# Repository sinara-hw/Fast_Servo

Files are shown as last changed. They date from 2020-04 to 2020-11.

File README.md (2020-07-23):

# Fast_Servo

High speed low latency servo (Stabilizer-compatible) module

## Design Files

Design files (schematics, PCB layouts, BOMs) can be found at [Fast_Servo/Releases](https://github.com/sinara-hw/Fast_Servo/releases).

## Wiki

More information can be found on the [wiki](https://github.com/sinara-hw/Fast_Servo/wiki).

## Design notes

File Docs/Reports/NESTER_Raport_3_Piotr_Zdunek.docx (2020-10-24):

Projekt „Niskolatencyjny, synchroniczny i skalowalny system SDR” (NESTER)

Piotr Zdunek

Raport z pracy o dzieło z prawami autorskimi pt.:
„ Opracowanie firmware FPGA dla modułu EEM z układem FPGA”
zrealizowanej w okresie od 04.05.2020 r. do 26.05.2020 r.
Pracę wykonał Piotr Zdunek

Celem pracy było opracowanie schematów i PCB modułu EEM z układem FPGA oraz symulacje systemu cyfrowego.

Trzeci etap prac zawierał następujące zadania:

- realizację schematów elektrycznych
- symulacje front-endu analogowego do przetwornika DAC
- projekt PCB

Wynikiem pracy są:

- Schematy elektryczne – ukończone w 100% - wymagają recenzji
  - https://github.com/sinara-hw/Fast_Servo/tree/master/PCB
- Projekt PCB – wstępne prace, ułożenie podstawowych komponentów, ustalenie ilości warstw
- Oprogramowanie testowe będzie przygotowane przy dalszym rozwinięciu projektu PCB
  - https://github.com/sinara-hw/Fast_Servo/tree/master/Sim/fast_servo
- Raport z symulacji front-endu przetwornika DAC (po angielsku)
  - https://docs.google.com/document/d/1JZjIepW1oN7cgWxagVTp9rN9icUm_Yqzp_lJ3G2Z5V4/edit?usp=sharing

1. Schematic:

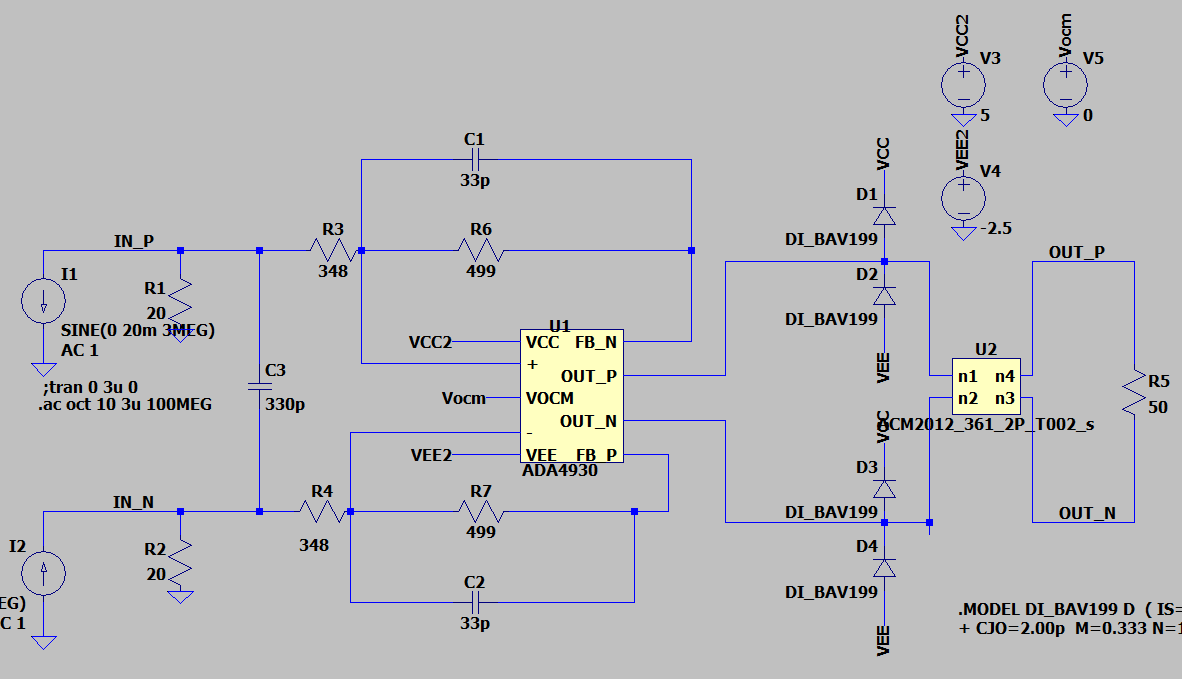
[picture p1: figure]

  1. Sim file for transient (with Monte Carlo simulation):

https://www.dropbox.com/s/zismo5z99h6hax0/ada4930_afe_tran_mc.asc?dl=0

  b. Sim file for AC(with Monte Carlo simulation):

https://www.dropbox.com/s/ytwsxa8ljqnvvi3/ada4930_afe_ac_mc.asc?dl=0

  c. Sim file for step (with Monte Carlo simulation) https://www.dropbox.com/s/y0xfj7qcieoy4dm/ada4930_afe_step_mc.asc?dl=0
2. Transient simulation:
    1. Common parameters: input signal is sinus for current sources
    2. Plot for 3 MHz 20 mA input signal

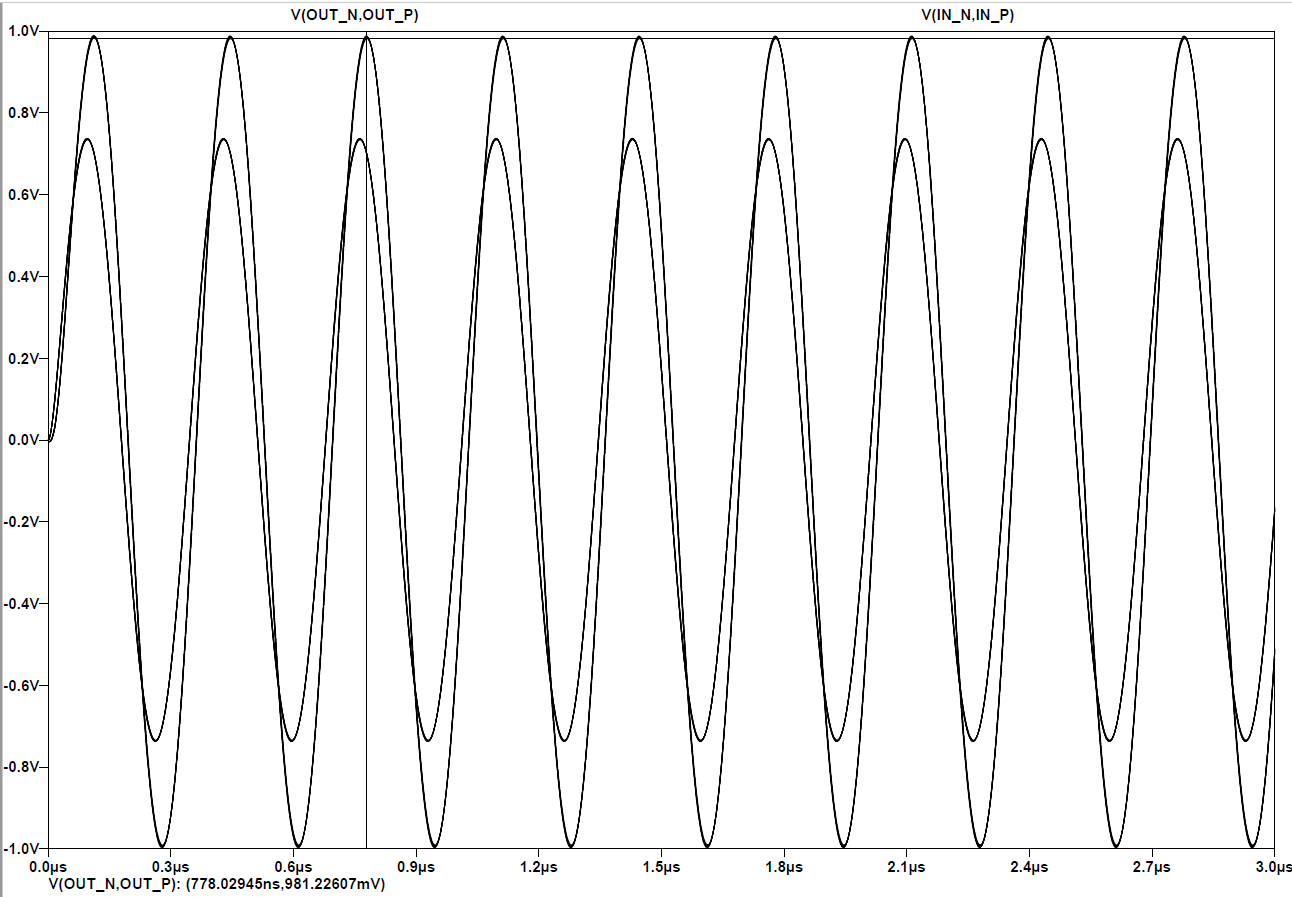
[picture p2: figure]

Simulation results:

Input signal | | Output signal
Freq [MHz] | Amplitude [mA] | Output amplitude [mV]
3 | 20 | 981
1 | 20 | 1059

3. AC simulation:

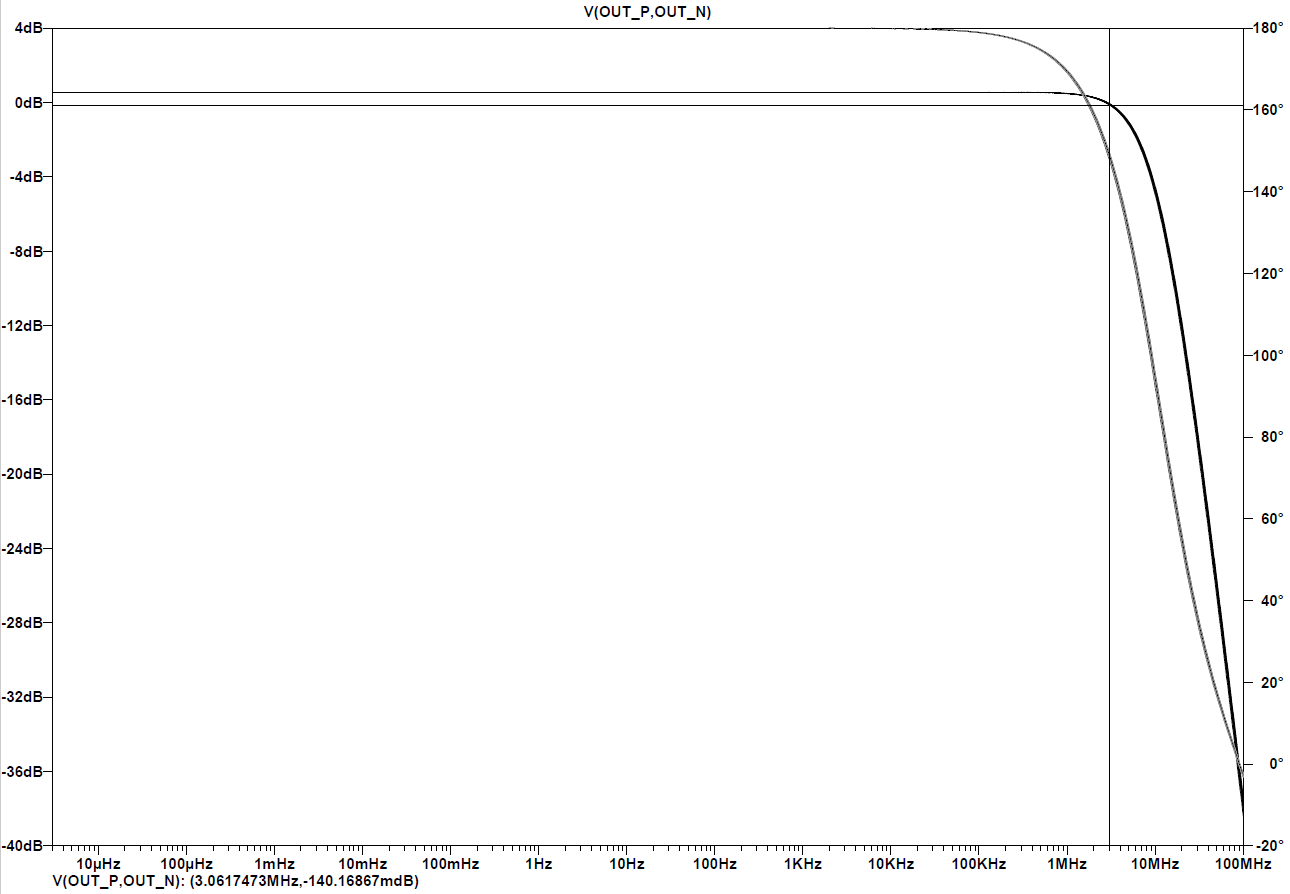
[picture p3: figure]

Simulation results:

Input signal amplitude [mA] | Attenuation at 1 MHz [dB] | Attenuation at 3 MHz [dB]
20 | 0.486 | -0.140

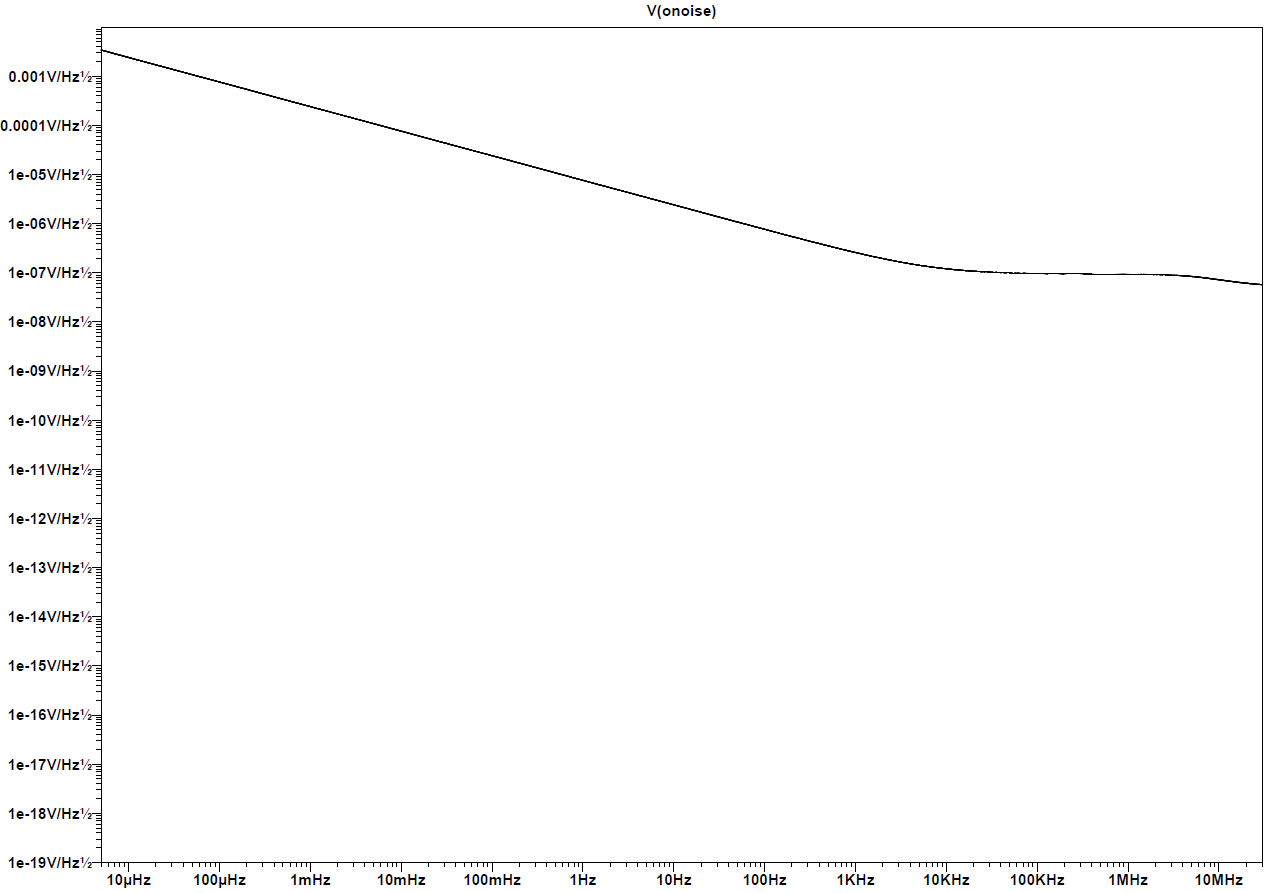
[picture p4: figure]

Plot for 1V input signal, Monte Carlo part value variance, 10 runs

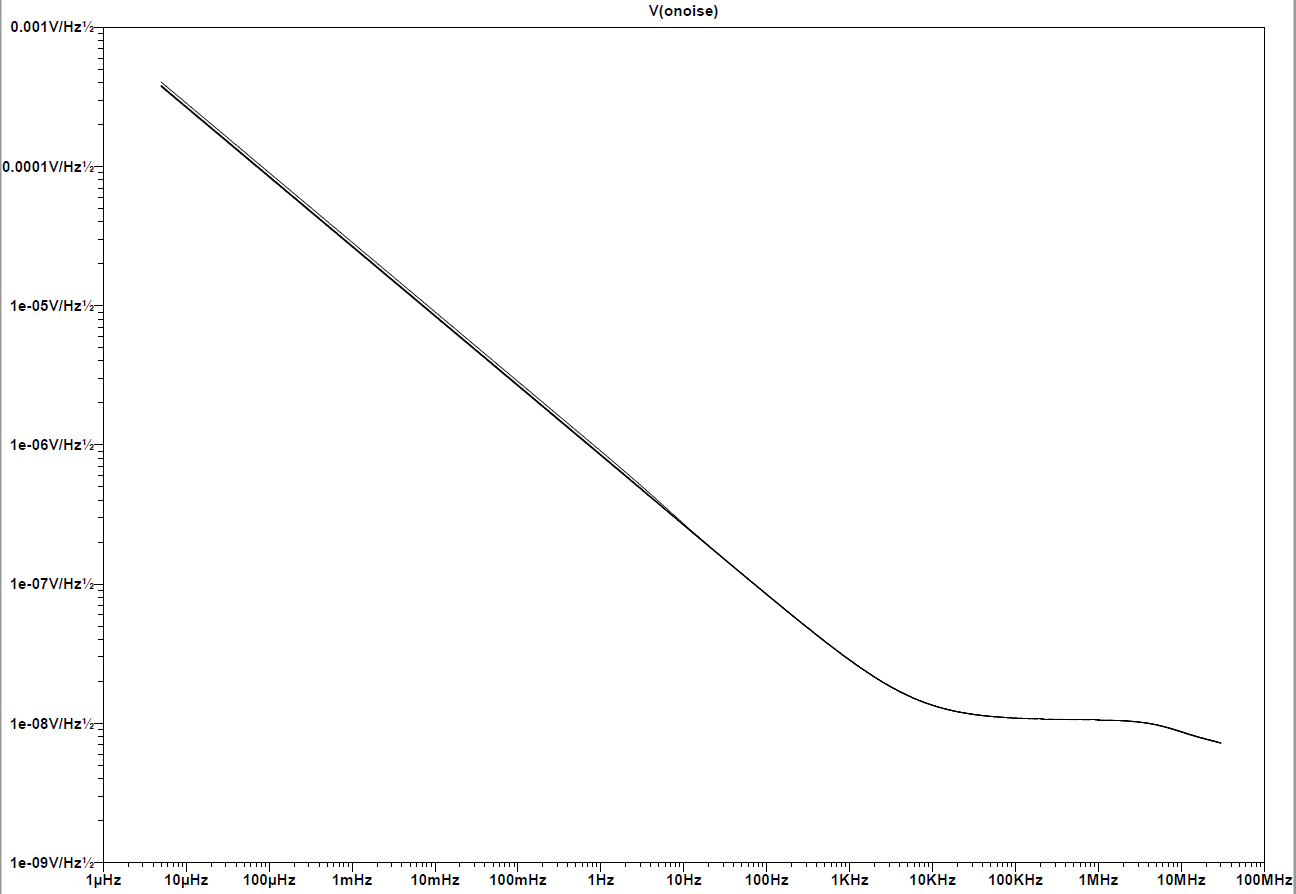
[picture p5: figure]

- Schemat elektryczny urządzenia zawierający dobrane komponenty:
  - Top schematic

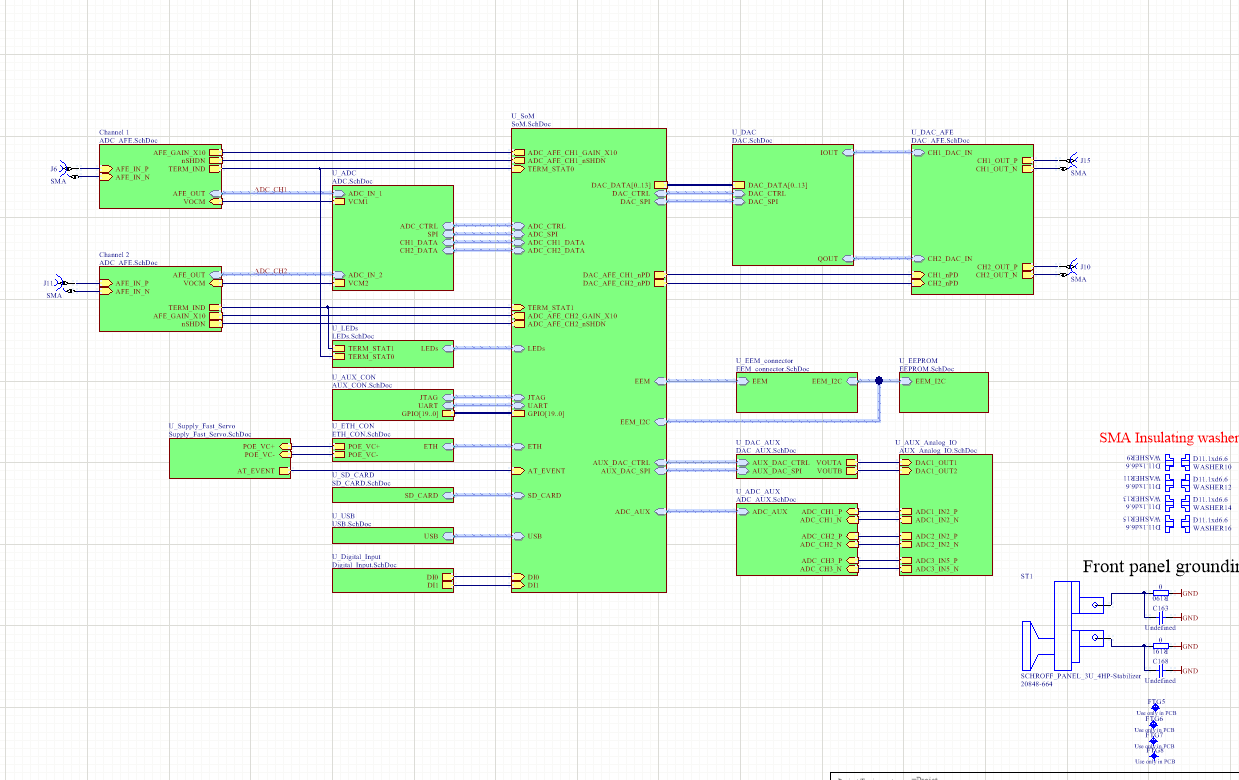
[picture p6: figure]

- ADC AFE

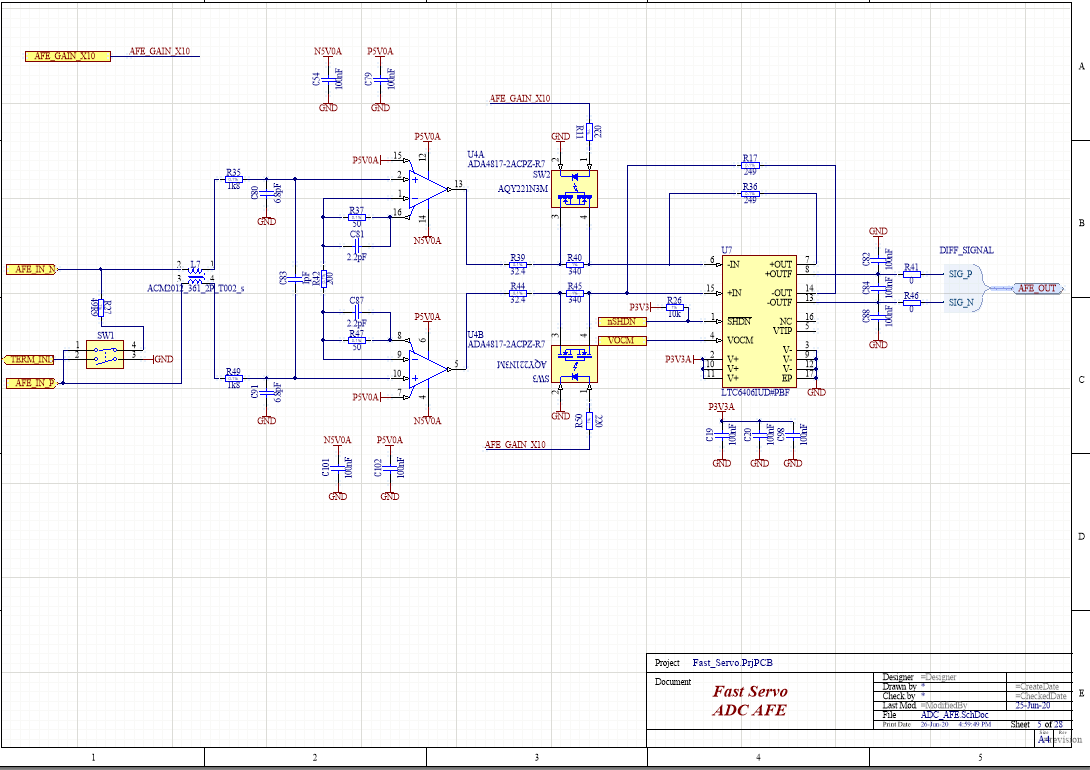
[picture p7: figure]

- DAC AFE

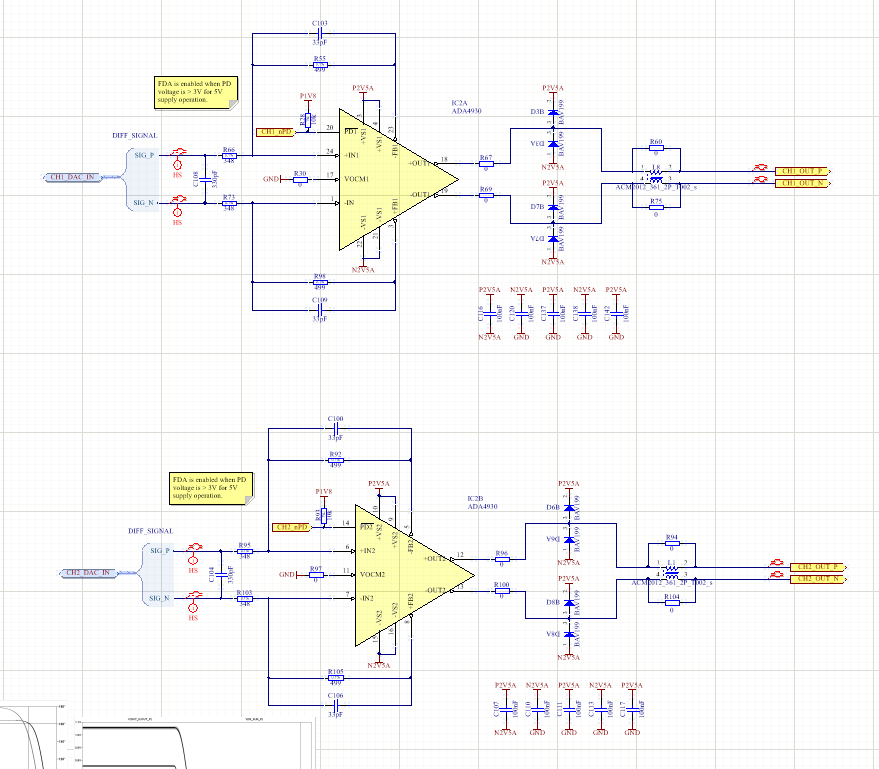
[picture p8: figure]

- PCB

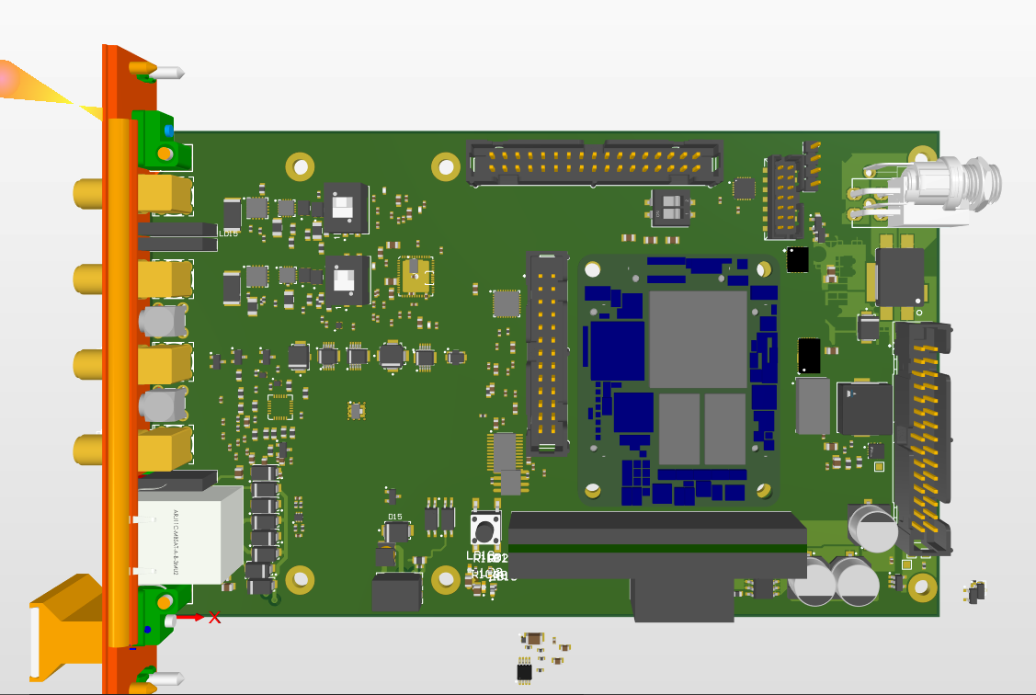
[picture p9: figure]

Spis treści

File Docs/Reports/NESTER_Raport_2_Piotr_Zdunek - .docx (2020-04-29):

Projekt „Niskolatencyjny, synchroniczny i skalowalny system SDR” (NESTER)

Piotr Zdunek

Raport z pracy o dzieło z prawami autorskimi pt.:
„ Opracowanie wzoru obwodu PCB oraz weryfikacja połączeń HDL modułu
EEM z układem FPGA”
zrealizowanej w okresie od 02.03.2020 r. do 28.04.2020 r.
Pracę wykonał Piotr Zdunek

Celem pracy było opracowanie schematów i PCB modułu EEM z układem FPGA oraz symulacje systemu cyfrowego.

Drugi etap prac zawierał następujące zadania:

- realizację schematów elektrycznych
- symulacje front-endu analogowego do przetwornika ADC
- symulacja systemu cyfrowego
- analiza opóźnienia odbioru danych

Wynikiem pracy są:

- Schematy elektryczne – ukończone w 70%
  - https://github.com/sinara-hw/Fast_Servo/tree/master/PCB
- Wstępny system cyfrowy do odbioru danych z LTC2195 oparty o design z projektu NIST Servo, ale z wykorzystaniem wrappera na VHDL
  - https://github.com/sinara-hw/Fast_Servo/tree/master/Sim/fast_servo

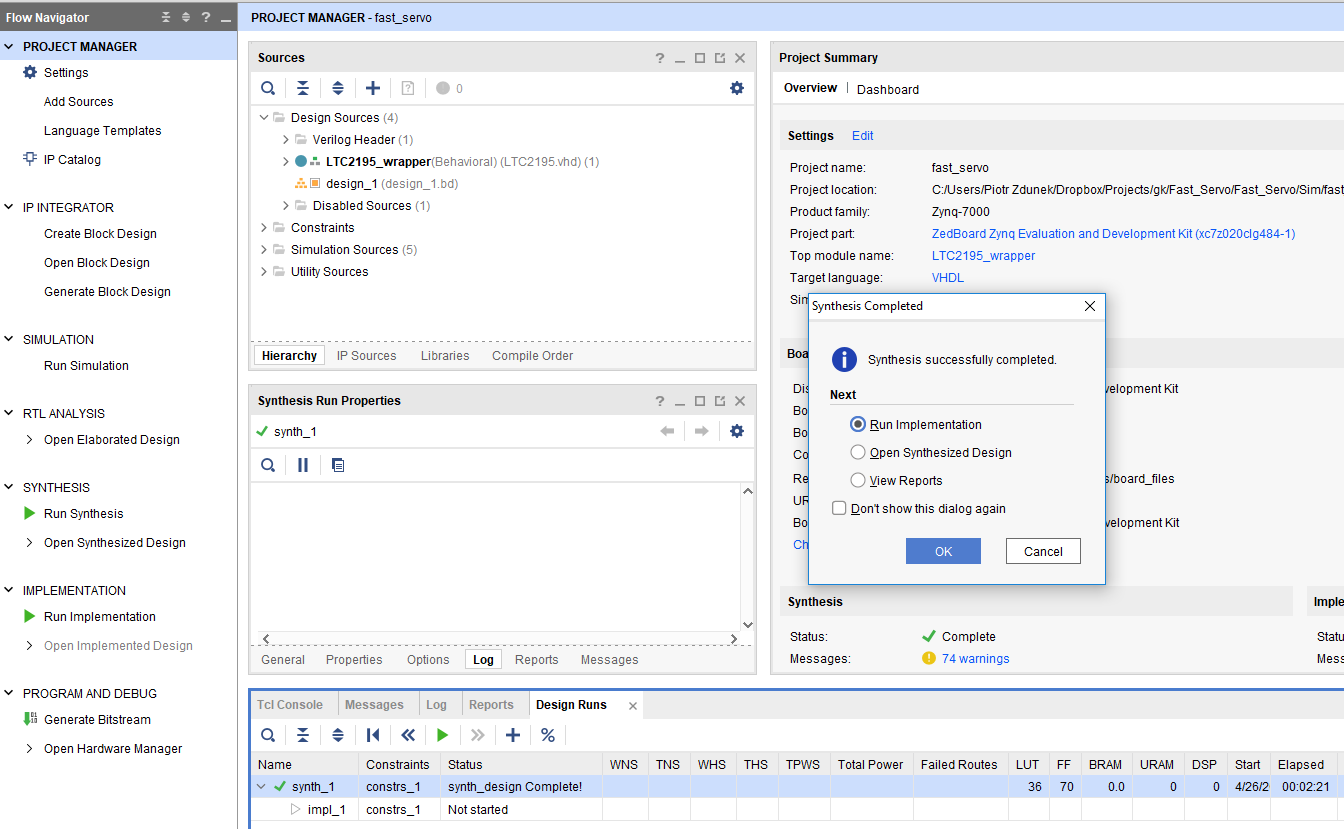
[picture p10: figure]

- Raport z symulacji front-endu przetwornika ADC (po angielsku)
  - https://docs.google.com/document/d/1smgiGiFC6XPziigHHxrSAG0CFXy-PrKfYR3dXpd6QYk/edit?usp=sharing

1. Variant 2 - RFI filter with common mode choke and differential low pass filter
  1. Schematic:

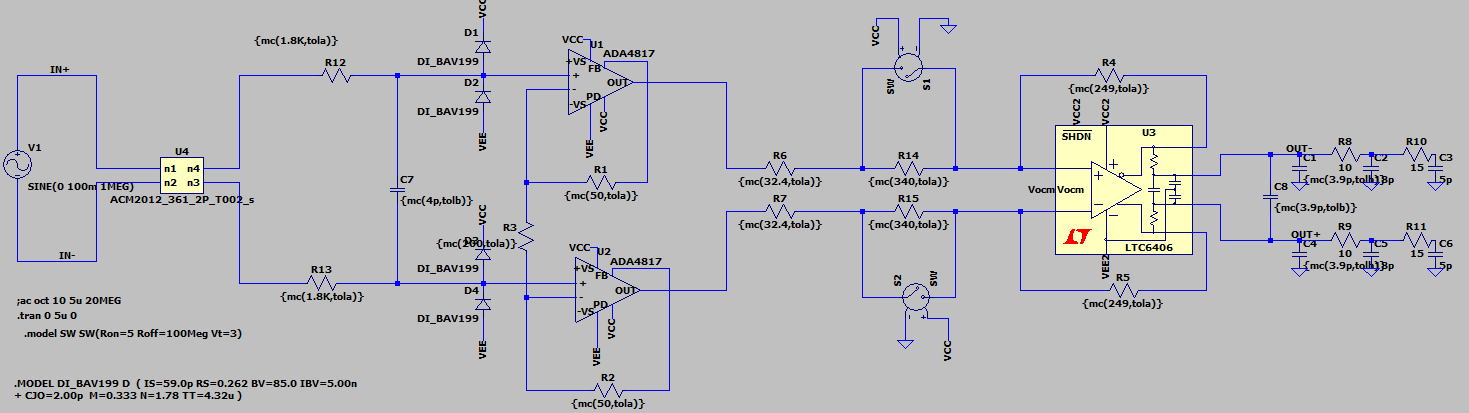
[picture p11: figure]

  b. Sim file for transient:

https://www.dropbox.com/s/ghg6t9eu0ng3u3w/fast_servo_tran_mc_v3.asc?dl=0

  c. Sim file for AC

https://www.dropbox.com/s/qx53d03kradoqxc/fast_servo_ac_v3.asc?dl=0

  d. Sim file for CMRR

https://www.dropbox.com/s/pwxwzrt2xnfyjam/fast_servo_cmrr_mc_v10.asc?dl=0

  e. Sim file for noise

https://www.dropbox.com/s/fyhz8l2sw5p7yvu/fast_servo_noise_mc_v3.asc?dl=0

Transient simulation:

Common parameters: input signal is sinus

Plot for 1 MHz 1 V input signal

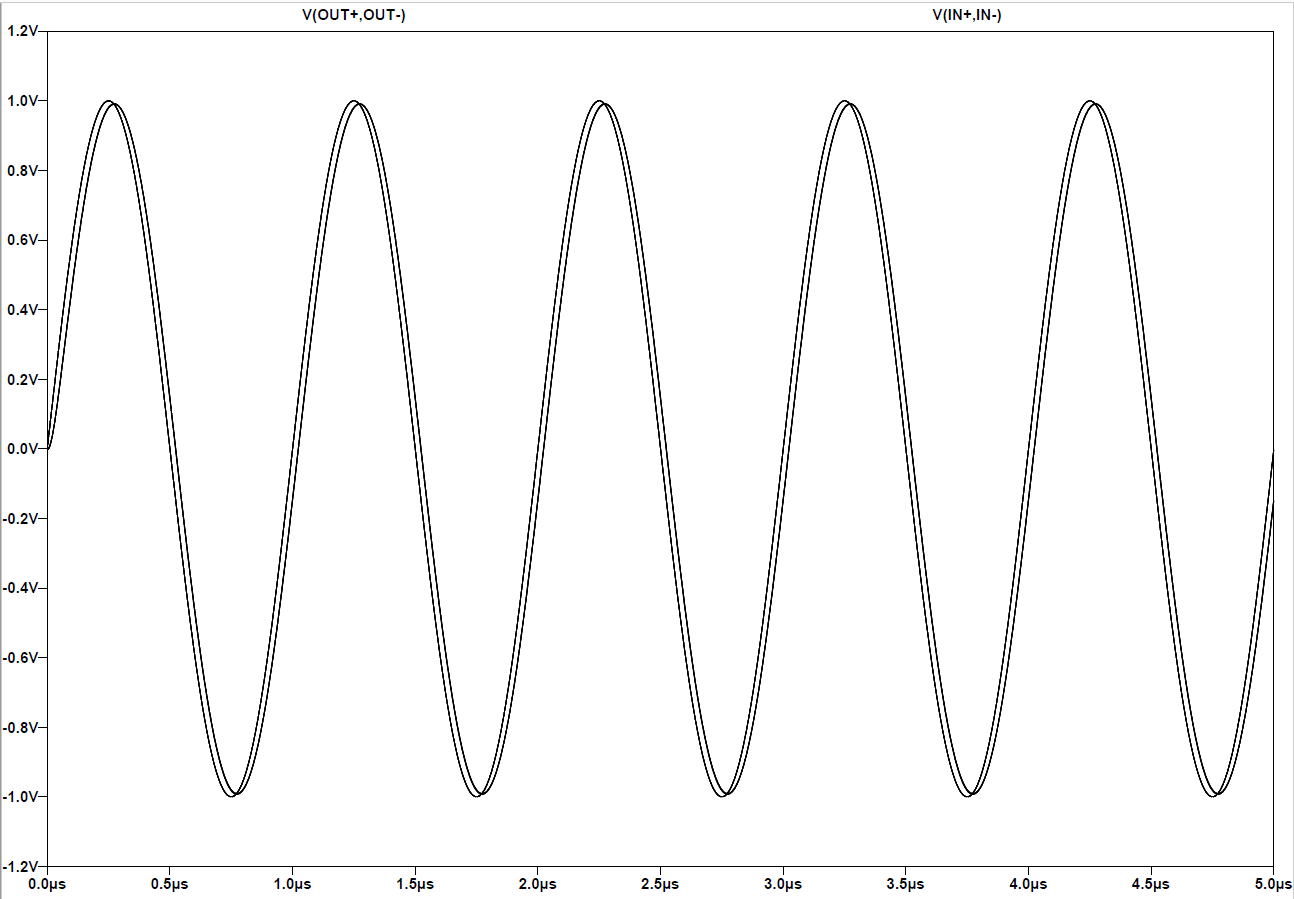
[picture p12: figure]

Simulation results:

Input signal | | AFE | Output signal
Freq [MHz] | Amplitude [mV] | Gain | Output amplitude [mV]
3 | 100 | x10 | 918
1 | 100 | x10 | 983
3 | 1000 | x1 | 925
1 | 1000 | x1 | 991

AC simulation:

Plot for 1V input signal, x1 gain

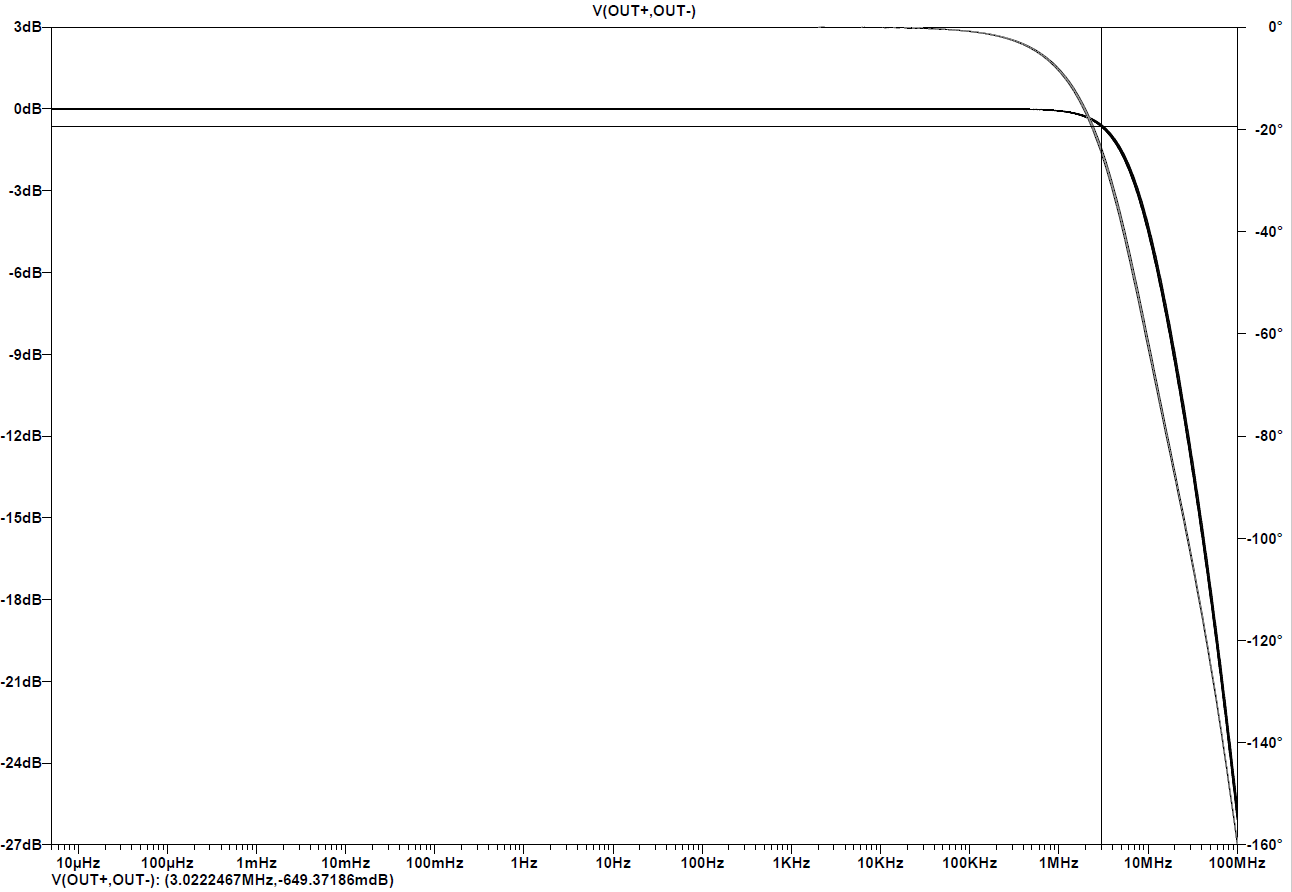
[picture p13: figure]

Simulation results:

Input signal amplitude [V] | AFE Gain | Attenuation at 1 MHz [dB] | Attenuation at 3 MHz [dB]
1 | x1 | -0.072 | -0.6
0.1 | x10 | -0.144 | -0.719

CMRR measurement:

Plot for 1 V input signal.

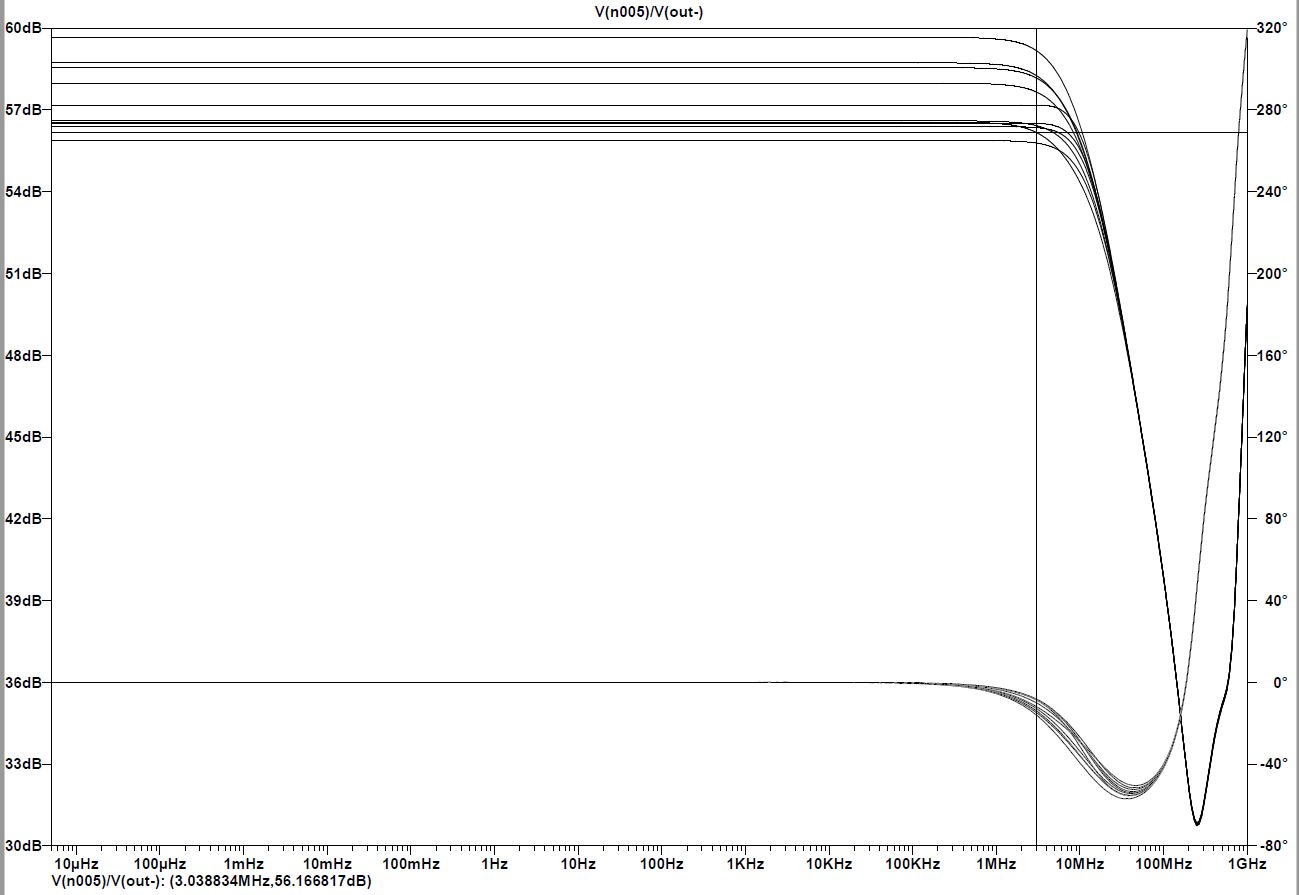
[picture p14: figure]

Simulation results:

Input signal amplitude [V] | AFE Gain | CMRR (0-3 MHz)
1 | x1 | 56 dB
0.1 | x10 | 49 dB

Noise

Plot for 100 mV input signal, Monte Carlo part value variance, 10 runs.


Plot for 1V input signal, Monte Carlo part value variance, 10 runs


- Analiza opóźnienia toru danych ADC-FPGA-DAC:

https://docs.google.com/document/d/1A6bej79ME2-iZyJ6t_FZ-XkVyk64ExRZh2uJX7Lg3b4/edit?usp=sharing

- Schemat elektryczny urządzenia zawierający dobrane komponenty:
  - Top schematic

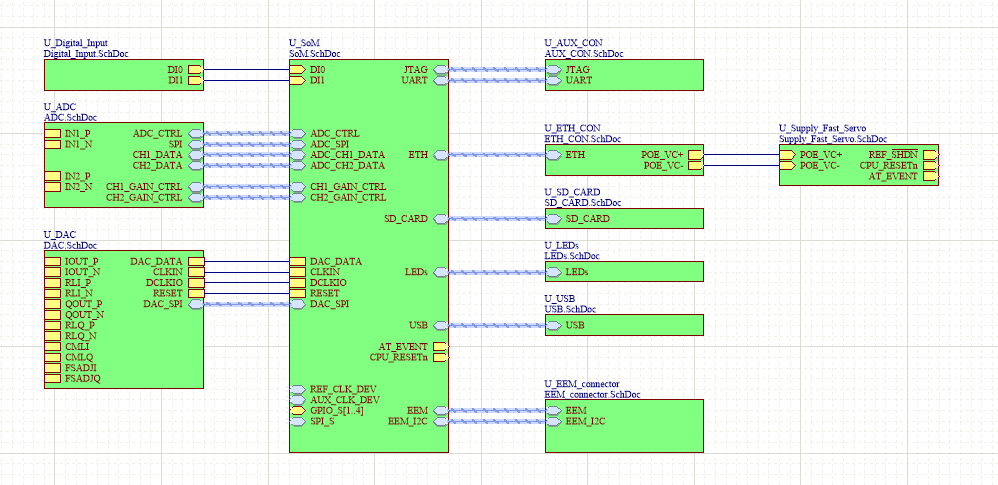
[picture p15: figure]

- Złącze Ethernet – 100 Mbps

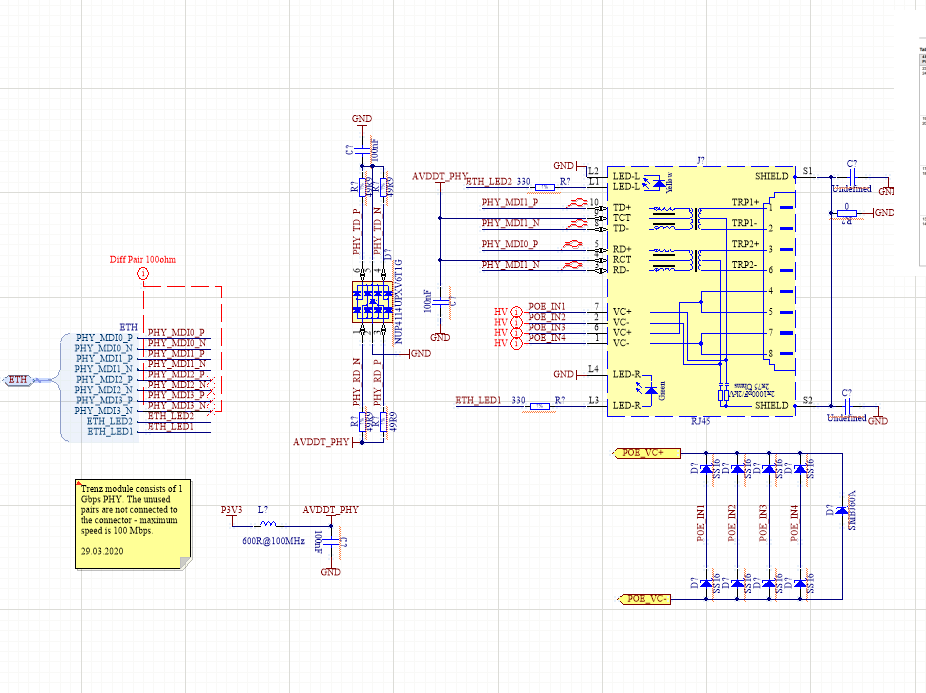
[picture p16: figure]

- USB

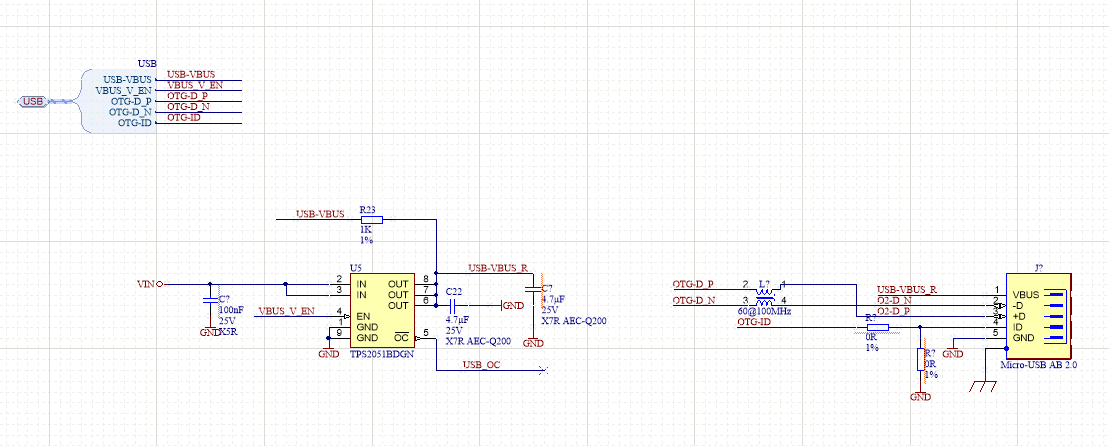
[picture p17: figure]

- SD Card

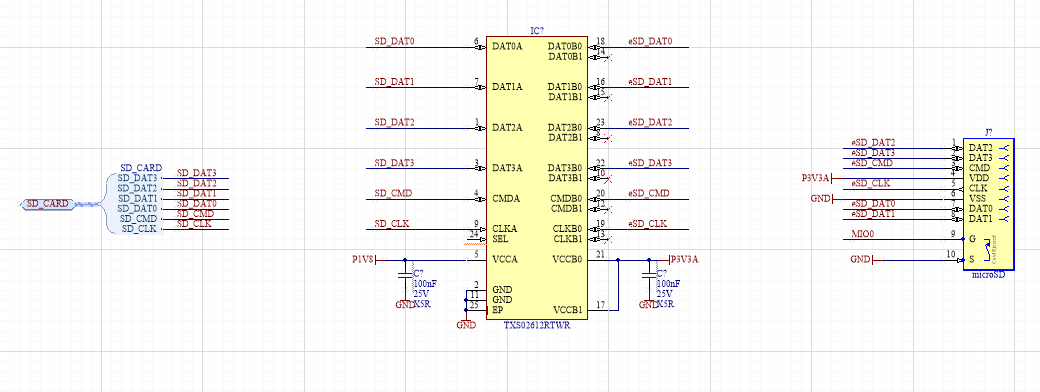
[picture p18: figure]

- AFE

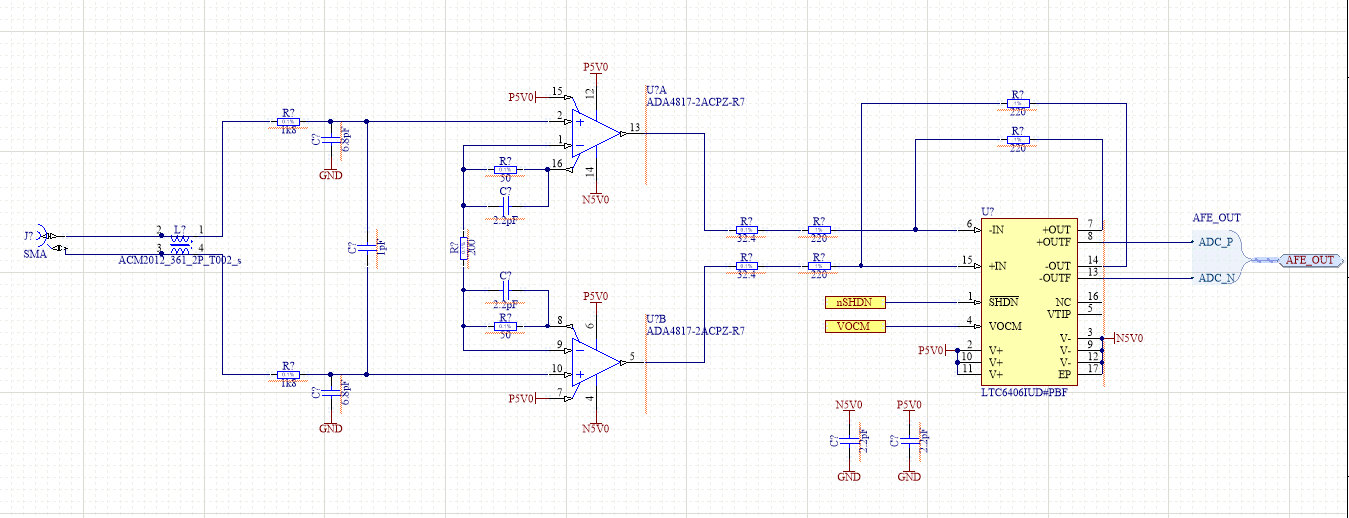
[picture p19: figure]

Spis treści

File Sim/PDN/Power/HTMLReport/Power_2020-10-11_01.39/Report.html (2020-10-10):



PDN Analyzer Results Report for
Fast_Servo

PDN Analyzer Version: 2.0.5.323
Report Time / Date: 11/10/2020 01:39:17
Project Name: Fast_Servo
Project Path: C:\Users\piotr\Downloads\temp\PCB\Fast_Servo.PCBDOC
PCB Design Name: Fast_Servo.PCBDOC
PDN Analyzer Configuration File: C:\Users\piotr\Downloads\temp\PCB\PDNAnalyzer_Output\Fast_Servo\Power\HTMLReport\Power_2020-10-11_01.39\Power.pdna

Design Stackup

Layer Name | Layer Name | Material | Thickness (mm) | Dielectric Material | Dielectric Constant | Pullback (mm) | Orientation
TopOverlay | Overlay | | | | | | Top
TopSolder | Solder Mask | Surface Material | 0.01016 | Solder Resist | 3.5 | | Top
Top | Signal | Copper | 0.05801 | | | | Top
Dielectric1 | Dielectric | Prepreg | 0.18 | PP-006 | 4.1
GP1(GND) | Internal | Copper | 0.035 | | | 0.508
Dielectric 3 | Dielectric | Core | 0.46 | Core-009 | 4.5
L3 | Signal | Copper | 0.035
Dielectric 2 | Dielectric | Prepreg | 0.18 | PP-006 | 4.1
L4 | Signal | Copper | 0.035
Dielectric 1 | Dielectric | Core | 0.46 | Core-009 | 4.5
P3V3 | Internal | Copper | 0.035 | | | 0.508
Dielectric2 | Dielectric | Prepreg | 0.18 | PP-006 | 4.1
Bot | Signal | Copper | 0.05801 | | | | Bottom
BottomSolder | Solder Mask | Surface Material | 0.01016 | Solder Resist | 3.5 | | Bottom
BottomOverlay | Overlay | | | | | | Bottom

Artwork by Layer

Layer: Top
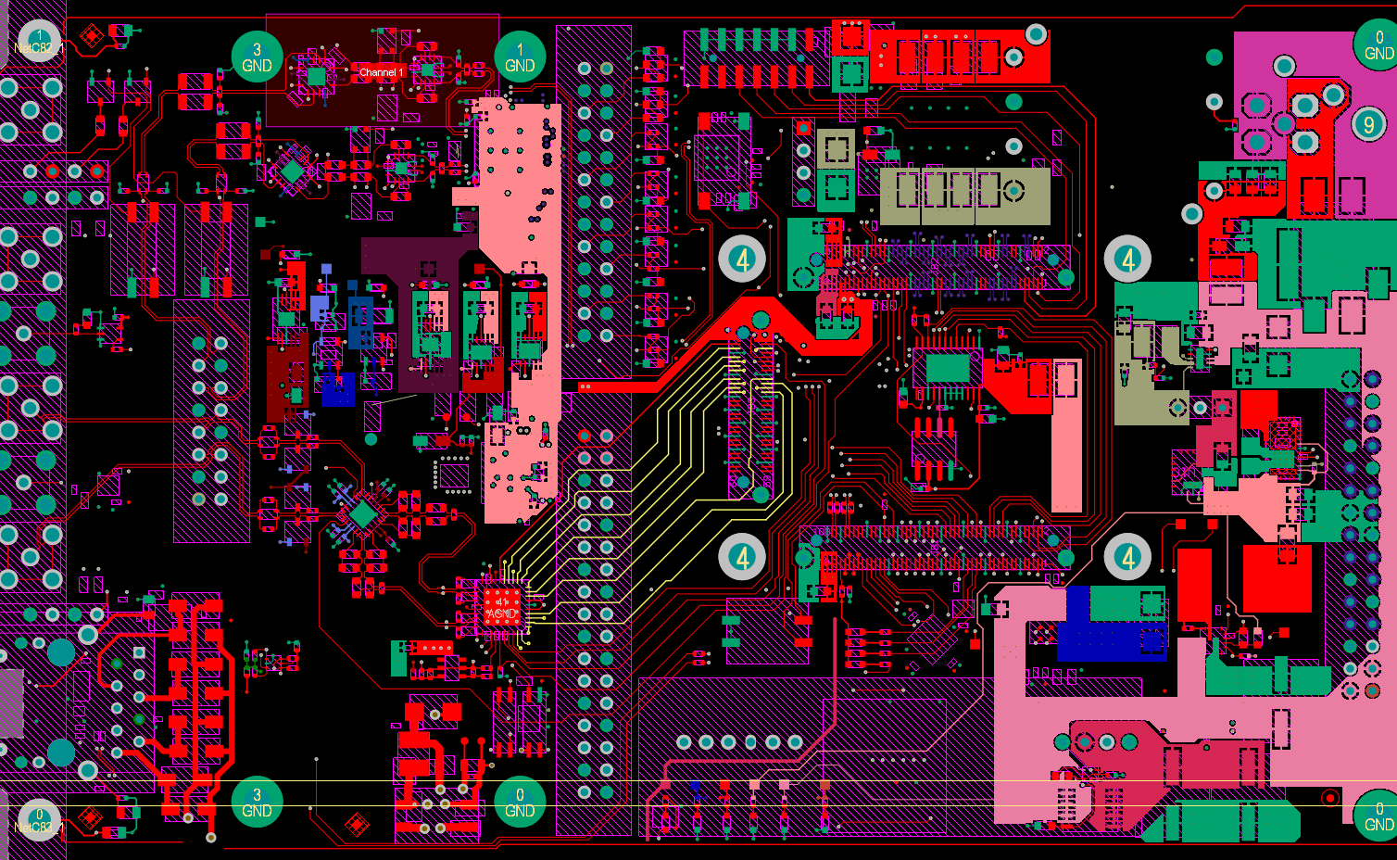
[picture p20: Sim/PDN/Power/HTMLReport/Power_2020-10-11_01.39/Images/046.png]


Layer: GP1(GND)
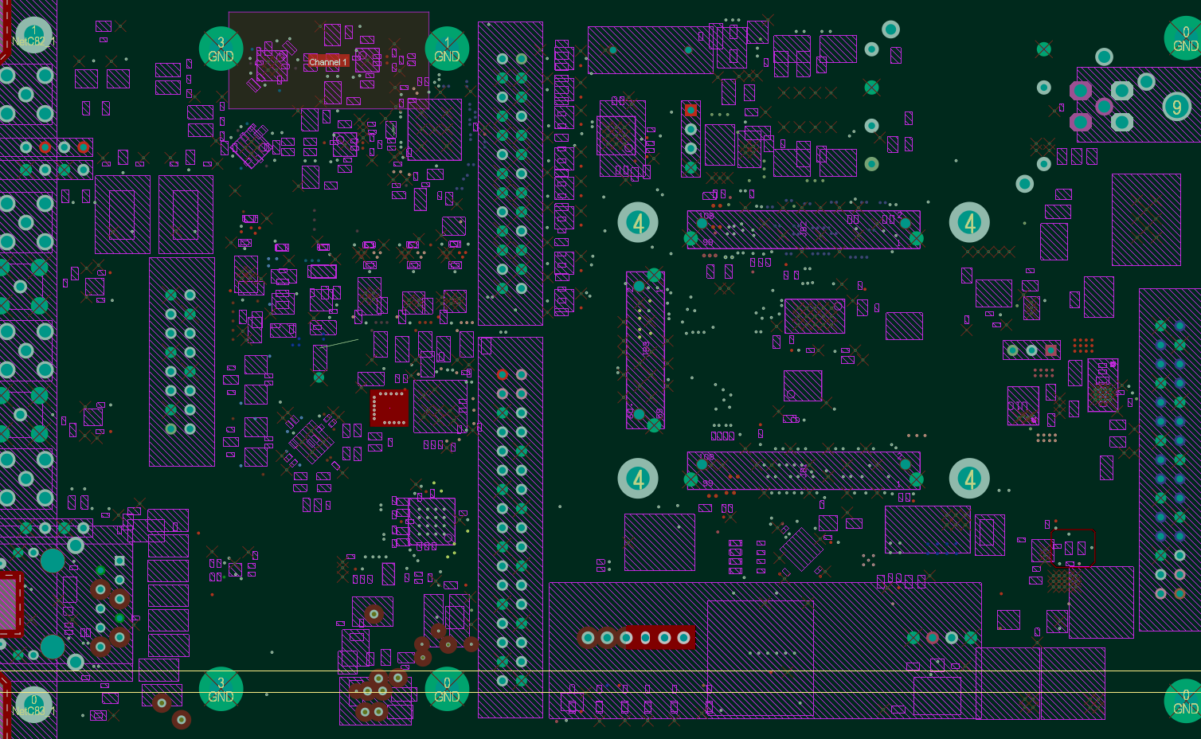
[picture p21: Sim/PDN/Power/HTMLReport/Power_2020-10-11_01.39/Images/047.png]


Layer: L3
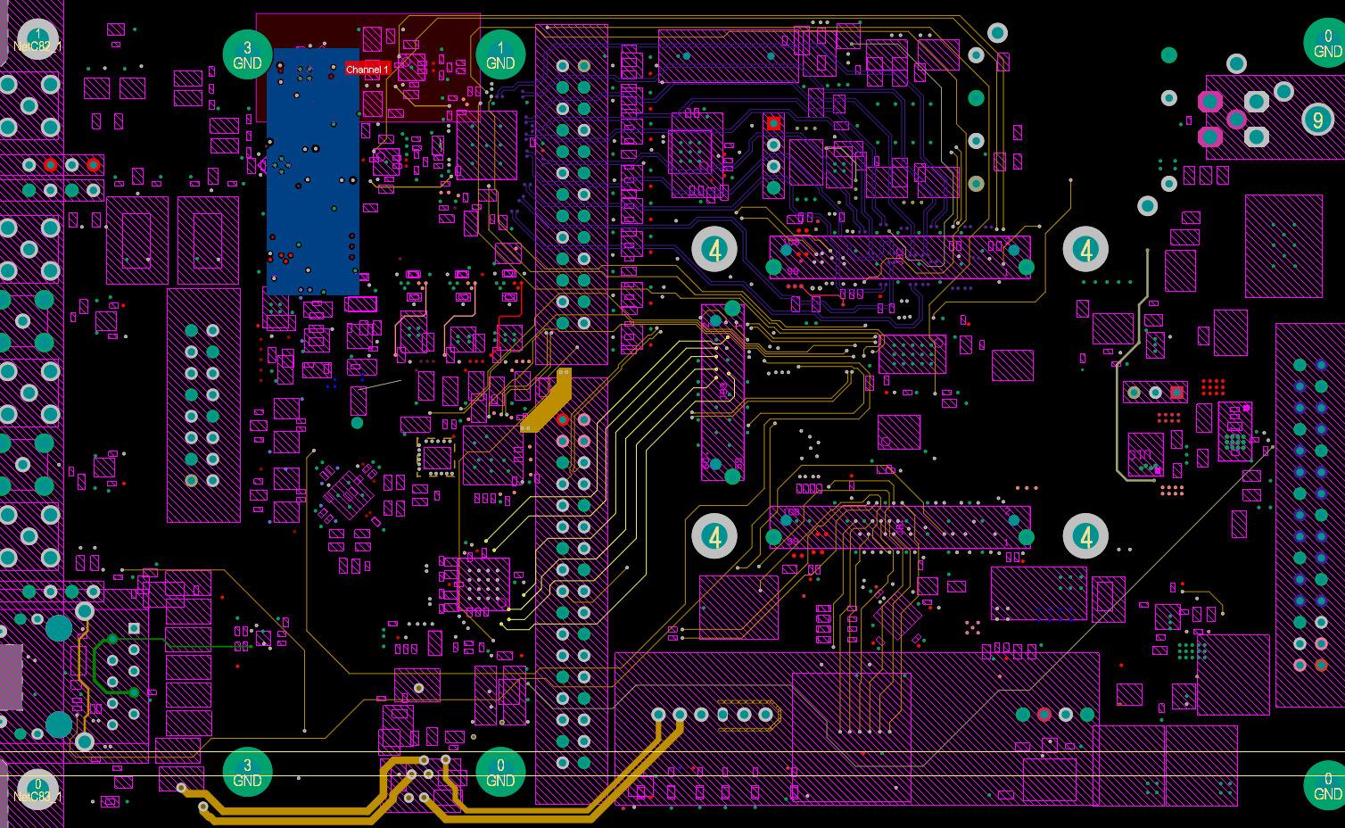
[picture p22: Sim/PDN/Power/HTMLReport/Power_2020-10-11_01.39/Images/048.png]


Layer: L4
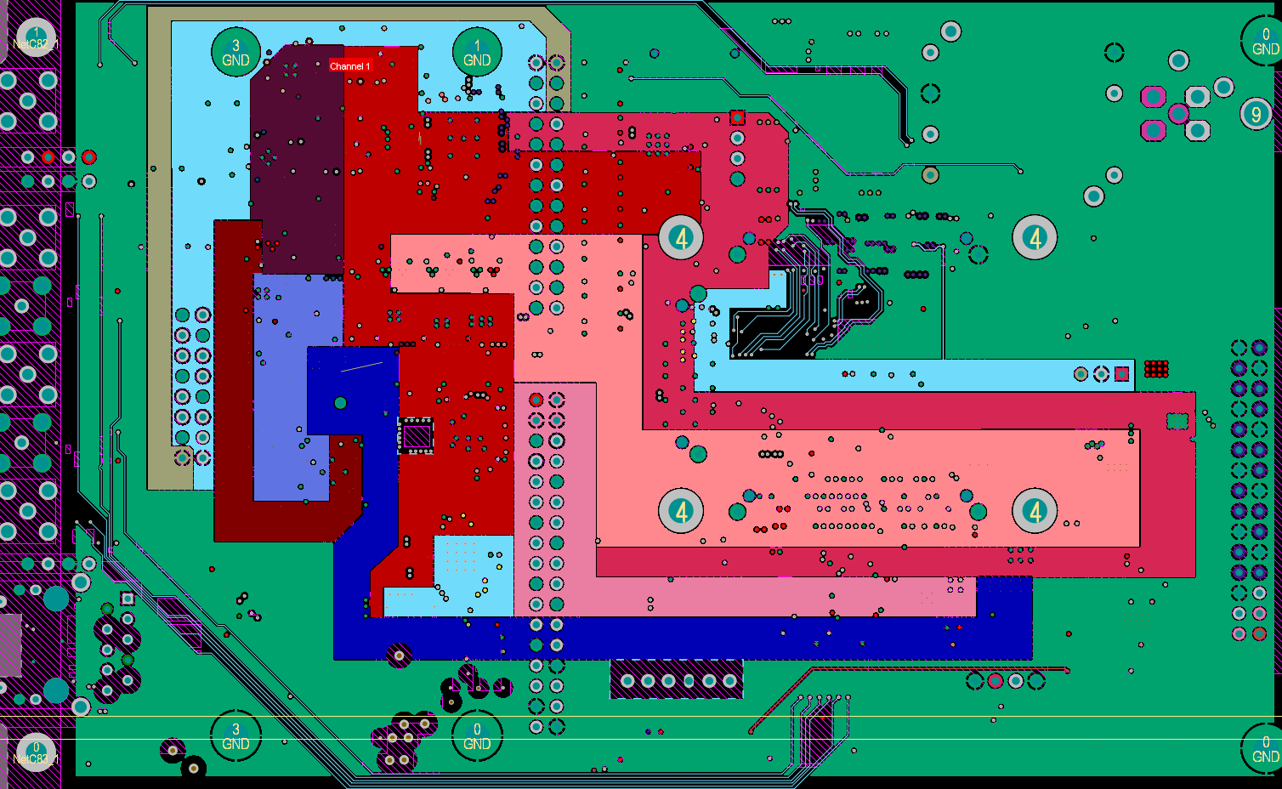
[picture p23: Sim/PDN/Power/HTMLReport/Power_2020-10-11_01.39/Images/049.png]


Layer: P3V3
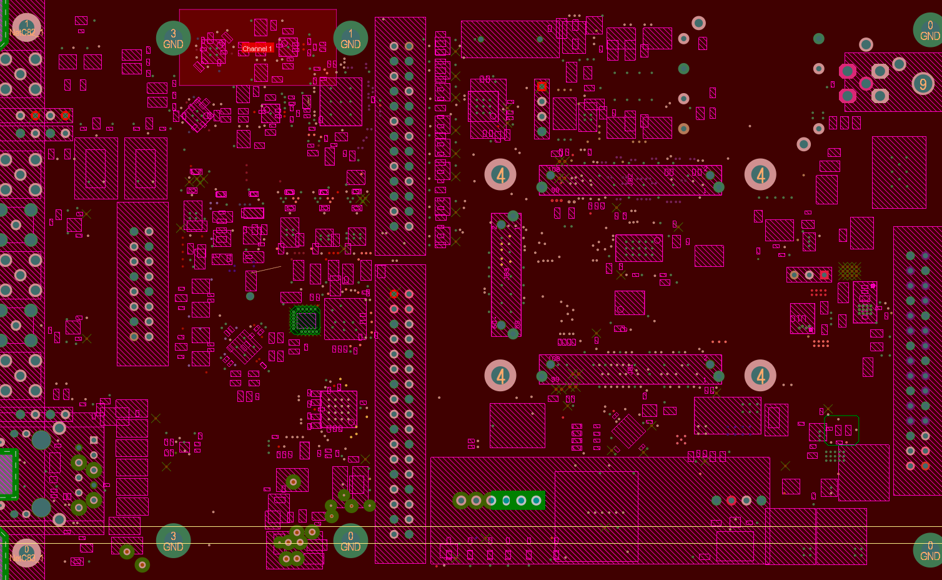
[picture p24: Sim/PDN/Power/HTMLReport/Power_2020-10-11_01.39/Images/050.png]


Layer: Bot


PDN Analizer Global Settings

Parameter | Value
Metal conductivity | 47M S/m
Metal base temperature | 3E+01 °C
Metal work temperature | 3E+01 °C
Metal base conductivity | 47M S/m
Metal temperature coefficient | 4E+02m %/°C
Conductor Max Current Density for Surfase Layers | 0 A/mm^2
Conductor Max Current Density for Internal Layers | 0 A/mm^2
Via wall thickness | 17.78 μm
Max Via Current Density | 0 A/mm^2

System-Level Power Network Results



Simulation Pass/Fail Overall: PASS
P2V5A PASS
P1V8A PASS
P3V3 PASS
P5V5 PASS
P1V8 PASS
P12V PASS
P3V3A PASS
P5V0A PASS
N2V5A PASS
N5V0A PASS
N5V5 PASS
P13V0S PASS
P12V0A PASS
N13V0S PASS
N12V0A PASS

Total Power Consumption: 26.5 Watts

Least Margins:

Margin Type | Absolute | Pass/Fail | Network | ID
Load Voltage (V) | 81.34m | PASS | P1V8 | Load 3
Voltage Source Current (A) | 0 | PASS | P12V0A | Source 1
Linear VRM Power Dissipation (W) | 610.01m | PASS | N2V5A | Source 1
Series Element Current (A) | 489.37m | PASS | P12V | Series 1

Margin Type (%) | Percent | Pass/Fail | Network | ID
Load Voltage | 4.76% | PASS | P1V8 | Load 3
Voltage Source Current | ∞ | PASS | P12V0A | Source 1
Linear VRM Power Dissipation | 61.00% | PASS | N2V5A | Source 1
Series Element Current | 48.94% | PASS | P12V | Series 1

Network P2V5A Details



PDN Analysis Pass/Fail: PASS

Power Consumption for This Network: 350m Watts

Least Margins:

Margin Type | Absolute | Pass/Fail | ID
Load Voltage (V) | 124m | PASS | Load 1
Voltage Source Current (A) | 60m | PASS | Source 1

Margin Type (%) | Percent | Pass/Fail | ID
Load Voltage | 5.22% | PASS | Load 1
Voltage Source Current | 30.00% | PASS | Source 1

Voltage Source Performance Summary:

ID | Source Type | Ref Des | Pass / Fail | Vout setting (V) | Actual Output Voltage (V) | Max Output Current (A) | Actual Output Current (A) | Margin (A) | Margin (%) | Max Pin Current | Highest Actual (A) | Margin (A) | Margin (%) | Max Power Dissipation (W) | Actual Power Dissipation (W) | Margin (W) | Margin (%)
Source 1 | Linear | IC9 | PASS | 2.5 | 2.5 | 200m | 140m | 60m | 30.00% | 0 | 70m | ∞ | ∞ | 0 | 112m | ∞ | ∞

Voltage Source Pin Voltage/Current Details:

ID | SourceType | Terminal | Ref Des | Pin | Max Pin Current (A) | Actual Pin Current (A) | Pass / Fail | Pin Voltage (V)
Source 1 | Linear | Out | IC9 | 9 | 0 | 70m | PASS | 2.5011
Source 1 | Linear | Out | IC9 | 10 | 0 | 70m | PASS | 2.5011
Source 1 | Linear | Ref | IC9 | 8 | 0 | 50u | PASS | 1.1412m
Source 1 | Linear | Ref | IC9 | 11 | 0 | 50u | PASS | 1.1411m

Load Performance Summary:

ID | Load Type | Ref Des | Pass / Fail | Load Value | Min Voltage (V) | Max Voltage (V) | Actual Voltage | Margin (V) | Margin (%) | Min Pwr Pin | Voltage (V) | Max Gnd Pin | Voltage (V) | Actual Current (A)
Load 1 | Current | IC3 | PASS | 130mA | 2.375 | 2.625 | 2.499 | 124m | 5.22% | IC3-10 | 2.5001 | IC3-25 | 1.1054m | 130m
Load 2 | Current | R106, LD6 | PASS | 10mA | 0 | 0 | 2.4997 | 0 | ∞ | R106-2 | 2.5009 | LD6-1 | 1.1782m | 10m

Load Pin Voltage/Current Details:

ID | Load Type | Terminal | Ref Des | Pin | Pin Voltage (V) | Pin Current (A)
Load 1 | Current | Power | IC3 | 10 | 2.5001 | 32.449m
Load 1 | Current | Power | IC3 | 9 | 2.5001 | 32.475m
Load 1 | Current | Power | IC3 | 4 | 2.5002 | 32.53m
Load 1 | Current | Power | IC3 | 3 | 2.5002 | 32.546m
Load 1 | Current | Ground | IC3 | 25 | 1.1054m | 130m
Load 2 | Current | Power | R106 | 2 | 2.5009 | 10m
Load 2 | Current | Ground | LD6 | 1 | 1.1782m | 10m

Component Definition Summary:

ID | Ref Des | Type | In+ Pins | In- Pins | Out+ Pins | Out- Pins | S+ | S- | Vout (V) | Efficiency (%) | Ibias (A) | Resistance | Load Current (A) | Vmin | Vmax | Iout max (A) | PD max (W) | Pin Current max (A)
Source 1 | IC9 | Linear | IC10-5-11 | IC9-8,11 | IC9-9,10 | | | | 2.5 | | 0 | | | | | 200m | 0
Load 1 | IC3 | Current | IC3-3,4,9,10 | IC3-25 | | | | | | | | | 130m | 2.375 | 2.625
Load 2 | R106, LD6 | Current | R106-2 | LD6-1 | | | | | | | | | 10m | 0 | 0

## Figure <1>: Current density



## Figure <2>: Voltage



Network P1V8A Details



PDN Analysis Pass/Fail: PASS

Power Consumption for This Network: 621m Watts

Least Margins:

Margin Type | Absolute | Pass/Fail | ID
Load Voltage (V) | 88.463m | PASS | Load 2
Voltage Source Current (A) | 155m | PASS | Source 1

Margin Type (%) | Percent | Pass/Fail | ID
Load Voltage | 5.17% | PASS | Load 2
Voltage Source Current | 31.00% | PASS | Source 1

Voltage Source Performance Summary:

ID | Source Type | Ref Des | Pass / Fail | Vout setting (V) | Actual Output Voltage (V) | Max Output Current (A) | Actual Output Current (A) | Margin (A) | Margin (%) | Max Pin Current | Highest Actual (A) | Margin (A) | Margin (%) | Max Power Dissipation (W) | Actual Power Dissipation (W) | Margin (W) | Margin (%)
Source 1 | Linear | IC16 | PASS | 1.8 | 1.8 | 500m | 345m | 155m | 31.00% | 0 | 172.5m | ∞ | ∞ | 0 | 517.02m | ∞ | ∞

Voltage Source Pin Voltage/Current Details:

ID | SourceType | Terminal | Ref Des | Pin | Max Pin Current (A) | Actual Pin Current (A) | Pass / Fail | Pin Voltage (V)
Source 1 | Linear | Out | IC16 | 10 | 0 | 172.5m | PASS | 1.8011
Source 1 | Linear | Out | IC16 | 9 | 0 | 172.5m | PASS | 1.8011
Source 1 | Linear | Ref | IC16 | 11 | 0 | 50u | PASS | 1.1378m
Source 1 | Linear | Ref | IC16 | 8 | 0 | 50u | PASS | 1.138m

Load Performance Summary:

ID | Load Type | Ref Des | Pass / Fail | Load Value | Min Voltage (V) | Max Voltage (V) | Actual Voltage | Margin (V) | Margin (%) | Min Pwr Pin | Voltage (V) | Max Gnd Pin | Voltage (V) | Actual Current (A)
Load 1 | Current | IC20 | PASS | 115mA | 1.71 | 1.89 | 1.7994 | 89.433m | 5.23% | IC20-40 | 1.8007 | IC20-45 | 1.2653m | 115m
Load 2 | Current | IC2 | PASS | 230mA | 1.71 | 1.89 | 1.7985 | 88.463m | 5.17% | IC2-15 | 1.7998 | IC2-33 | 1.3853m | 230m

Load Pin Voltage/Current Details:

ID | Load Type | Terminal | Ref Des | Pin | Pin Voltage (V) | Pin Current (A)
Load 1 | Current | Power | IC20 | 18 | 1.8008 | 14.401m
Load 1 | Current | Power | IC20 | 21 | 1.8008 | 14.409m
Load 1 | Current | Power | IC20 | 26 | 1.8008 | 14.399m
Load 1 | Current | Power | IC20 | 29 | 1.8008 | 14.388m
Load 1 | Current | Power | IC20 | 32 | 1.8008 | 14.379m
Load 1 | Current | Power | IC20 | 34 | 1.8008 | 14.375m
Load 1 | Current | Power | IC20 | 39 | 1.8007 | 14.328m
Load 1 | Current | Power | IC20 | 40 | 1.8007 | 14.322m
Load 1 | Current | Ground | IC20 | 45 | 1.2653m | 115m
Load 2 | Current | Power | IC2 | 15 | 1.7998 | 57.483m
Load 2 | Current | Power | IC2 | 16 | 1.7998 | 57.484m
Load 2 | Current | Power | IC2 | 51 | 1.7999 | 57.486m
Load 2 | Current | Power | IC2 | 52 | 1.8 | 57.546m
Load 2 | Current | Ground | IC2 | 53 | 1.2978m | 25.568m
Load 2 | Current | Ground | IC2 | 2 | 1.3156m | 25.561m
Load 2 | Current | Ground | IC2 | 5 | 1.315m | 25.561m
Load 2 | Current | Ground | IC2 | 13 | 1.3281m | 25.556m
Load 2 | Current | Ground | IC2 | 22 | 1.3174m | 25.56m
Load 2 | Current | Ground | IC2 | 33 | 1.3853m | 25.532m
Load 2 | Current | Ground | IC2 | 45 | 1.3315m | 25.554m
Load 2 | Current | Ground | IC2 | 47 | 1.3333m | 25.554m
Load 2 | Current | Ground | IC2 | 49 | 1.3318m | 25.554m

Component Definition Summary:

ID | Ref Des | Type | In+ Pins | In- Pins | Out+ Pins | Out- Pins | S+ | S- | Vout (V) | Efficiency (%) | Ibias (A) | Resistance | Load Current (A) | Vmin | Vmax | Iout max (A) | PD max (W) | Pin Current max (A)
Source 1 | IC16 | Linear | IC10-5-11 | IC16-8,11 | IC16-9,10 | | | | 1.8 | | 0 | | | | | 500m | 0
Load 1 | IC20 | Current | IC20-18,21,26,29,32,34,39,40 | IC20-45 | | | | | | | | | 115m | 1.71 | 1.89
Load 2 | IC2 | Current | IC2-15,16,51,52 | IC2-2,5,13,22,33,45,47,49,53 | | | | | | | | | 230m | 1.71 | 1.89

## Figure <3>: Current density



## Figure <4>: Voltage



Network P3V3 Details



PDN Analysis Pass/Fail: PASS

Power Consumption for This Network: 4.38 Watts

Least Margins:

Margin Type | Absolute | Pass/Fail | ID
Load Voltage (V) | 160.67m | PASS | Load 2
Voltage Source Current (A) | 2.3798 | PASS | Source 1

Margin Type (%) | Percent | Pass/Fail | ID
Load Voltage | 5.13% | PASS | Load 2
Voltage Source Current | 59.50% | PASS | Source 1

Voltage Source Performance Summary:

ID | Source Type | Ref Des | Pass / Fail | Vout setting (V) | Actual Output Voltage (V) | Max Output Current (A) | Actual Output Current (A) | Margin (A) | Margin (%) | Max Pin Current | Highest Actual (A) | Margin (A) | Margin (%) | Max Power Dissipation (W) | Actual Power Dissipation (W) | Margin (W) | Margin (%)
Source 1 | SMPS | IC10 | PASS | 3.3 | 3.2984 | 4 | 1.6202 | 2.3798 | 59.50% | 0 | 271.94m | ∞ | ∞

Voltage Source Pin Voltage/Current Details:

ID | SourceType | Terminal | Ref Des | Pin | Max Pin Current (A) | Actual Pin Current (A) | Pass / Fail | Pin Voltage (V)
Source 1 | SMPS | Out+ | IC10 | 5 | 0 | 231.46m | PASS | 3.2988
Source 1 | SMPS | Out+ | IC10 | 6 | 0 | 231.46m | PASS | 3.2988
Source 1 | SMPS | Out+ | IC10 | 7 | 0 | 231.46m | PASS | 3.2988
Source 1 | SMPS | Out+ | IC10 | 8 | 0 | 231.46m | PASS | 3.2988
Source 1 | SMPS | Out+ | IC10 | 9 | 0 | 231.46m | PASS | 3.2988
Source 1 | SMPS | Out+ | IC10 | 10 | 0 | 231.46m | PASS | 3.2988
Source 1 | SMPS | Out+ | IC10 | 11 | 0 | 231.46m | PASS | 3.2988
Source 1 | SMPS | Out- | IC10 | 26 | 0 | 180.02m | PASS | 396.08u
Source 1 | SMPS | Out- | IC10 | 26 | 0 | 120.11m | PASS | 396.08u
Source 1 | SMPS | Out- | IC10 | 13 | 0 | 180.02m | PASS | 396.08u
Source 1 | SMPS | Out- | IC10 | 13 | 0 | 120.11m | PASS | 396.08u
Source 1 | SMPS | Out- | IC10 | 14 | 0 | 180.02m | PASS | 396.08u
Source 1 | SMPS | Out- | IC10 | 14 | 0 | 120.11m | PASS | 396.08u
Source 1 | SMPS | Out- | IC10 | 15 | 0 | 180.02m | PASS | 396.08u
Source 1 | SMPS | Out- | IC10 | 15 | 0 | 120.11m | PASS | 396.08u
Source 1 | SMPS | Out- | IC10 | 16 | 0 | 180.02m | PASS | 396.08u
Source 1 | SMPS | Out- | IC10 | 16 | 0 | 120.11m | PASS | 396.08u
Source 1 | SMPS | Out- | IC10 | 17 | 0 | 180.02m | PASS | 396.08u
Source 1 | SMPS | Out- | IC10 | 17 | 0 | 120.11m | PASS | 396.08u
Source 1 | SMPS | Out- | IC10 | 18 | 0 | 180.02m | PASS | 396.08u
Source 1 | SMPS | Out- | IC10 | 18 | 0 | 120.11m | PASS | 396.08u
Source 1 | SMPS | Out- | IC10 | 32 | 0 | 180.02m | PASS | 396.08u
Source 1 | SMPS | Out- | IC10 | 32 | 0 | 120.11m | PASS | 396.08u
Source 1 | SMPS | Out- | IC10 | 39 | 0 | 180.02m | PASS | 396.08u
Source 1 | SMPS | Out- | IC10 | 39 | 0 | 120.11m | PASS | 396.08u

Load Performance Summary:

ID | Load Type | Ref Des | Pass / Fail | Load Value | Min Voltage (V) | Max Voltage (V) | Actual Voltage | Margin (V) | Margin (%) | Min Pwr Pin | Voltage (V) | Max Gnd Pin | Voltage (V) | Actual Current (A)
Load 1 | Current | JB1 | PASS | 500mA | 3.135 | 3.465 | 3.296 | 161.04m | 5.14% | JB1-2 | 3.297 | JB1-1 | 1.0124m | 500m
Load 2 | Current | JB2 | PASS | 500mA | 3.135 | 3.465 | 3.2957 | 160.67m | 5.13% | JB2-7 | 3.297 | JB2-49 | 1.3077m | 500m
Load 3 | Current | IC4 | PASS | 1mA | 3.135 | 3.465 | 3.2963 | 161.34m | 5.15% | IC4-5 | 3.2975 | IC4-3 | 1.1299m | 1m
Load 4 | Current | IC5 | PASS | 1mA | 3.135 | 3.465 | 3.2963 | 161.35m | 5.15% | IC5-5 | 3.2975 | IC5-3 | 1.1189m | 1m
Load 5 | Current | IC15 | PASS | 16mA | 3.135 | 3.465 | 3.2967 | 161.74m | 5.16% | IC15-4 | 3.2975 | IC15-2 | 779.36u | 16m
Load 6 | Current | IC6 | PASS | 5mA | 3.135 | 3.465 | 3.2968 | 161.78m | 5.16% | IC6-21 | 3.2975 | IC6-2 | 760.53u | 5m
Load 7 | Current | IC1 | PASS | 1mA | 3.135 | 3.465 | 3.2964 | 161.37m | 5.15% | IC1-3 | 3.2975 | IC1-9 | 1.0935m | 1m
Load 8 | Current | J4 | PASS | 100mA | 3.135 | 3.465 | 3.2963 | 161.26m | 5.14% | J4-34 | 3.2974 | J4-30 | 1.1049m | 100m
Load 9 | Current | U6 | PASS | 6mA | 3.135 | 3.465 | 3.2963 | 161.32m | 5.15% | U6-32 | 3.2975 | U6-6 | 1.1447m | 6m
Load 10 | Current | U7 | PASS | 5mA | 3.135 | 3.465 | 3.2965 | 161.52m | 5.15% | U7-14 | 3.2975 | U7-1 | 1.0097m | 5m
Load 11 | Linear | IC10, IC9 | | | | | 3.2976 | | | IC10-5 | 3.2988 | IC9-8 | 1.1412m | 140.1m
Load 12 | Linear | IC10, IC16 | | | | | 3.2976 | | | IC10-5 | 3.2988 | IC16-8 | 1.138m | 345.1m

Load Pin Voltage/Current Details:

ID | Load Type | Terminal | Ref Des | Pin | Pin Voltage (V) | Pin Current (A)
Load 1 | Current | Power | JB1 | 16 | 3.2972 | 71.453m
Load 1 | Current | Power | JB1 | 14 | 3.2972 | 71.45m
Load 1 | Current | Power | JB1 | 12 | 3.2971 | 71.447m
Load 1 | Current | Power | JB1 | 10 | 3.2971 | 71.442m
Load 1 | Current | Power | JB1 | 6 | 3.2971 | 71.407m
Load 1 | Current | Power | JB1 | 4 | 3.2971 | 71.404m
Load 1 | Current | Power | JB1 | 2 | 3.297 | 71.398m
Load 1 | Current | Ground | JB1 | F1 | 943.12u | 27.755m
Load 1 | Current | Ground | JB1 | F2 | 655.12u | 27.898m
Load 1 | Current | Ground | JB1 | 54 | 866.28u | 27.793m
Load 1 | Current | Ground | JB1 | 53 | 922.32u | 27.765m
Load 1 | Current | Ground | JB1 | 43 | 962.04u | 27.746m
Load 1 | Current | Ground | JB1 | 33 | 962.68u | 27.745m
Load 1 | Current | Ground | JB1 | 30 | 920.44u | 27.766m
Load 1 | Current | Ground | JB1 | 25 | 975.97u | 27.739m
Load 1 | Current | Ground | JB1 | 19 | 1.0028m | 27.725m
Load 1 | Current | Ground | JB1 | 7 | 1.0075m | 27.723m
Load 1 | Current | Ground | JB1 | 1 | 1.0124m | 27.721m
Load 1 | Current | Ground | JB1 | 63 | 918.88u | 27.767m
Load 1 | Current | Ground | JB1 | 64 | 875.01u | 27.789m
Load 1 | Current | Ground | JB1 | 73 | 868.35u | 27.792m
Load 1 | Current | Ground | JB1 | 74 | 811.69u | 27.82m
Load 1 | Current | Ground | JB1 | 83 | 863.35u | 27.795m
Load 1 | Current | Ground | JB1 | 89 | 816.98u | 27.818m
Load 1 | Current | Ground | JB1 | 90 | 761.6u | 27.845m
Load 2 | Current | Power | JB2 | 7 | 3.297 | 124.99m
Load 2 | Current | Power | JB2 | 5 | 3.297 | 125m
Load 2 | Current | Power | JB2 | 3 | 3.297 | 125m
Load 2 | Current | Power | JB2 | 1 | 3.297 | 125.01m
Load 2 | Current | Ground | JB2 | F1 | 1.1341m | 33.42m
Load 2 | Current | Ground | JB2 | F2 | 976.07u | 33.545m
Load 2 | Current | Ground | JB2 | 60 | 1.2842m | 33.301m
Load 2 | Current | Ground | JB2 | 59 | 1.2934m | 33.293m
Load 2 | Current | Ground | JB2 | 50 | 1.2827m | 33.302m
Load 2 | Current | Ground | JB2 | 49 | 1.3077m | 33.282m
Load 2 | Current | Ground | JB2 | 40 | 1.2796m | 33.304m
Load 2 | Current | Ground | JB2 | 39 | 1.288m | 33.298m
Load 2 | Current | Ground | JB2 | 29 | 1.2937m | 33.293m
Load 2 | Current | Ground | JB2 | 19 | 1.2922m | 33.294m
Load 2 | Current | Ground | JB2 | 69 | 1.2749m | 33.308m
Load 2 | Current | Ground | JB2 | 70 | 1.242m | 33.334m
Load 2 | Current | Ground | JB2 | 79 | 1.2587m | 33.321m
Load 2 | Current | Ground | JB2 | 80 | 1.2435m | 33.333m
Load 2 | Current | Ground | JB2 | 89 | 1.1956m | 33.371m
Load 3 | Current | Power | IC4 | 5 | 3.2975 | 1m
Load 3 | Current | Ground | IC4 | 3 | 1.1299m | 1m
Load 4 | Current | Power | IC5 | 5 | 3.2975 | 1m
Load 4 | Current | Ground | IC5 | 3 | 1.1189m | 1m
Load 5 | Current | Power | IC15 | 4 | 3.2975 | 16m
Load 5 | Current | Ground | IC15 | 2 | 779.36u | 16m
Load 6 | Current | Power | IC6 | 21 | 3.2975 | 2.4997m
Load 6 | Current | Power | IC6 | 17 | 3.2976 | 2.5003m
Load 6 | Current | Ground | IC6 | 11 | 759.78u | 1.6667m
Load 6 | Current | Ground | IC6 | 2 | 760.53u | 1.6667m
Load 6 | Current | Ground | IC6 | 25 | 758.89u | 1.6667m
Load 7 | Current | Power | IC1 | 3 | 3.2975 | 500u
Load 7 | Current | Power | IC1 | 2 | 3.2975 | 500u
Load 7 | Current | Ground | IC1 | 9 | 1.0935m | 500u
Load 7 | Current | Ground | IC1 | 1 | 1.0924m | 500u
Load 8 | Current | Power | J4 | 34 | 3.2974 | 100m
Load 8 | Current | Ground | J4 | 10 | 981.08u | 10.014m
Load 8 | Current | Ground | J4 | 7 | 947.19u | 10.033m
Load 8 | Current | Ground | J4 | 4 | 944.87u | 10.034m
Load 8 | Current | Ground | J4 | 1 | 916.32u | 10.05m
Load 8 | Current | Ground | J4 | 19 | 1.03m | 9.9873m
Load 8 | Current | Ground | J4 | 16 | 1.0253m | 9.9899m
Load 8 | Current | Ground | J4 | 13 | 989.28u | 10.01m
Load 8 | Current | Ground | J4 | 30 | 1.1049m | 9.9461m
Load 8 | Current | Ground | J4 | 25 | 1.0655m | 9.9678m
Load 8 | Current | Ground | J4 | 22 | 1.065m | 9.9681m
Load 9 | Current | Power | U6 | 32 | 3.2975 | 3m
Load 9 | Current | Power | U6 | 31 | 3.2975 | 3.0001m
Load 9 | Current | Ground | U6 | 33 | 1.1362m | 1.0001m
Load 9 | Current | Ground | U6 | 29 | 1.1383m | 1.0001m
Load 9 | Current | Ground | U6 | 19 | 1.1397m | 1m
Load 9 | Current | Ground | U6 | 6 | 1.1447m | 999.92u
Load 9 | Current | Ground | U6 | 5 | 1.1436m | 999.94u
Load 9 | Current | Ground | U6 | 1 | 1.1409m | 999.99u
Load 10 | Current | Power | U7 | 14 | 3.2975 | 5m
Load 10 | Current | Ground | U7 | 25 | 986.47u | 713.87u
Load 10 | Current | Ground | U7 | 15 | 985.99u | 713.88u
Load 10 | Current | Ground | U7 | 18 | 953.75u | 714.8u
Load 10 | Current | Ground | U7 | 19 | 954.92u | 714.77u
Load 10 | Current | Ground | U7 | 20 | 955.73u | 714.75u
Load 10 | Current | Ground | U7 | 21 | 956.01u | 714.74u
Load 10 | Current | Ground | U7 | 1 | 1.0097m | 713.2u
Load 11 | Linear | In | IC10 | 5 | 3.2988 | 14.286u
Load 11 | Linear | In | IC10 | 5 | 3.2988 | 20m
Load 11 | Linear | In | IC10 | 6 | 3.2988 | 14.286u
Load 11 | Linear | In | IC10 | 6 | 3.2988 | 20m
Load 11 | Linear | In | IC10 | 7 | 3.2988 | 14.286u
Load 11 | Linear | In | IC10 | 7 | 3.2988 | 20m
Load 11 | Linear | In | IC10 | 8 | 3.2988 | 14.286u
Load 11 | Linear | In | IC10 | 8 | 3.2988 | 20m
Load 11 | Linear | In | IC10 | 9 | 3.2988 | 14.286u
Load 11 | Linear | In | IC10 | 9 | 3.2988 | 20m
Load 11 | Linear | In | IC10 | 10 | 3.2988 | 14.286u
Load 11 | Linear | In | IC10 | 10 | 3.2988 | 20m
Load 11 | Linear | In | IC10 | 11 | 3.2988 | 14.286u
Load 11 | Linear | In | IC10 | 11 | 3.2988 | 20m
Load 11 | Linear | Ref | IC9 | 8 | 1.1412m | 50u
Load 11 | Linear | Ref | IC9 | 11 | 1.1411m | 50u
Load 12 | Linear | In | IC10 | 5 | 3.2988 | 14.286u
Load 12 | Linear | In | IC10 | 5 | 3.2988 | 49.286m
Load 12 | Linear | In | IC10 | 6 | 3.2988 | 14.286u
Load 12 | Linear | In | IC10 | 6 | 3.2988 | 49.286m
Load 12 | Linear | In | IC10 | 7 | 3.2988 | 14.286u
Load 12 | Linear | In | IC10 | 7 | 3.2988 | 49.286m
Load 12 | Linear | In | IC10 | 8 | 3.2988 | 14.286u
Load 12 | Linear | In | IC10 | 8 | 3.2988 | 49.286m
Load 12 | Linear | In | IC10 | 9 | 3.2988 | 14.286u
Load 12 | Linear | In | IC10 | 9 | 3.2988 | 49.286m
Load 12 | Linear | In | IC10 | 10 | 3.2988 | 14.286u
Load 12 | Linear | In | IC10 | 10 | 3.2988 | 49.286m
Load 12 | Linear | In | IC10 | 11 | 3.2988 | 14.286u
Load 12 | Linear | In | IC10 | 11 | 3.2988 | 49.286m
Load 12 | Linear | Ref | IC16 | 11 | 1.1378m | 50u
Load 12 | Linear | Ref | IC16 | 8 | 1.138m | 50u

Component Definition Summary:

ID | Ref Des | Type | In+ Pins | In- Pins | Out+ Pins | Out- Pins | S+ | S- | Vout (V) | Efficiency (%) | Ibias (A) | Resistance | Load Current (A) | Vmin | Vmax | Iout max (A) | PD max (W) | Pin Current max (A)
Source 1 | IC10 | SMPS
Load 1 | JB1 | Current | JB1-2,4,6,10,12,14,16 | JB1-F1,F2,54,53,43,33,30,25,19,7,1,63,64,73,74,83,89,90 | | | | | | | | | 500m | 3.135 | 3.465
Load 2 | JB2 | Current | JB2-1,3,5,7 | JB2-F1,F2,60,59,50,49,40,39,29,19,69,70,79,80,89 | | | | | | | | | 500m | 3.135 | 3.465
Load 3 | IC4 | Current | IC4-5 | IC4-3 | | | | | | | | | 1m | 3.135 | 3.465
Load 4 | IC5 | Current | IC5-5 | IC5-3 | | | | | | | | | 1m | 3.135 | 3.465
Load 5 | IC15 | Current | IC15-4 | IC15-2 | | | | | | | | | 16m | 3.135 | 3.465
Load 6 | IC6 | Current | IC6-17,21 | IC6-2,11,25 | | | | | | | | | 5m | 3.135 | 3.465
Load 7 | IC1 | Current | IC1-2,3 | IC1-1,9 | | | | | | | | | 1m | 3.135 | 3.465
Load 8 | J4 | Current | J4-34 | J4-1,4,7,10,13,16,19,22,25,30 | | | | | | | | | 100m | 3.135 | 3.465
Load 9 | U6 | Current | U6-31,32 | U6-1,5,6,19,29,33 | | | | | | | | | 6m | 3.135 | 3.465
Load 10 | U7 | Current | U7-14 | U7-1,15,18-21,25 | | | | | | | | | 5m | 3.135 | 3.465
Load 11 | IC10, IC9 | Linear | IC10-5-11 | IC9-8,11 | IC9-9,10 | | | | 2.5 | | 0 | | | | | 200m | 0 | 70m
Load 12 | IC10, IC16 | Linear | IC10-5-11 | IC16-8,11 | IC16-9,10 | | | | 1.8 | | 0 | | | | | 500m | 0 | 172.5m

## Figure <5>: Screenshot 012



## Figure <6>: Current density



Network P5V5 Details



PDN Analysis Pass/Fail: PASS

Power Consumption for This Network: 1.3 Watts

Least Margins:

Margin Type | Absolute | Pass/Fail | ID
Voltage Source Current (A) | 4.3331 | PASS | Source 1

Margin Type (%) | Percent | Pass/Fail | ID
Voltage Source Current | 72.22% | PASS | Source 1

Voltage Source Performance Summary:

ID | Source Type | Ref Des | Pass / Fail | Vout setting (V) | Actual Output Voltage (V) | Max Output Current (A) | Actual Output Current (A) | Margin (A) | Margin (%) | Max Pin Current | Highest Actual (A) | Margin (A) | Margin (%) | Max Power Dissipation (W) | Actual Power Dissipation (W) | Margin (W) | Margin (%)
Source 1 | SMPS | R139, IC11 | PASS | 5.5 | 5.4983 | 6 | 1.6669 | 4.3331 | 72.22% | 0 | 1.6669 | ∞ | ∞

Voltage Source Pin Voltage/Current Details:

ID | SourceType | Terminal | Ref Des | Pin | Max Pin Current (A) | Actual Pin Current (A) | Pass / Fail | Pin Voltage (V)
Source 1 | SMPS | Out+ | R139 | 2 | 0 | 1.6669 | PASS | 5.4983
Source 1 | SMPS | Out- | IC11 | 9 | 0 | 1.6669 | PASS | 12.03u
Source 1 | SMPS | Out- | IC11 | 9 | 0 | 899.42m | PASS | 12.03u

Load Performance Summary:

ID | Load Type | Ref Des | Pass / Fail | Load Value | Min Voltage (V) | Max Voltage (V) | Actual Voltage | Margin (V) | Margin (%) | Min Pwr Pin | Voltage (V) | Max Gnd Pin | Voltage (V) | Actual Current (A)
Load 1 | SMPS | IC10 | | | | | 5.493 | | | IC10-33 | 5.4934 | IC10-26 | 396.08u | 1.081
Load 2 | SMPS | U10 | | | | | 5.4962 | | | U10-18 | 5.4966 | U10-21 | 387.37u | 234.7m
Load 3 | Linear | IC18 | | | | | 5.4927 | | | IC18-6 | 5.4938 | IC18-5 | 1.1477m | 233.1m
Load 4 | Linear | IC19 | | | | | 5.4929 | | | IC19-1 | 5.4941 | IC19-11 | 1.1459m | 118.1m

Load Pin Voltage/Current Details:

ID | Load Type | Terminal | Ref Des | Pin | Pin Voltage (V) | Pin Current (A)
Load 1 | SMPS | In+ | IC10 | 20 | 5.4969 | 271.94m
Load 1 | SMPS | In+ | IC10 | 21 | 5.4969 | 271.92m
Load 1 | SMPS | In+ | IC10 | 19 | 5.4969 | 271.94m
Load 1 | SMPS | In+ | IC10 | 33 | 5.4934 | 265.19m
Load 1 | SMPS | In- | IC10 | 26 | 396.08u | 180.02m
Load 1 | SMPS | In- | IC10 | 26 | 396.08u | 120.11m
Load 1 | SMPS | In- | IC10 | 13 | 396.08u | 180.02m
Load 1 | SMPS | In- | IC10 | 13 | 396.08u | 120.11m
Load 1 | SMPS | In- | IC10 | 14 | 396.08u | 180.02m
Load 1 | SMPS | In- | IC10 | 14 | 396.08u | 120.11m
Load 1 | SMPS | In- | IC10 | 15 | 396.08u | 180.02m
Load 1 | SMPS | In- | IC10 | 15 | 396.08u | 120.11m
Load 1 | SMPS | In- | IC10 | 16 | 396.08u | 180.02m
Load 1 | SMPS | In- | IC10 | 16 | 396.08u | 120.11m
Load 1 | SMPS | In- | IC10 | 17 | 396.08u | 180.02m
Load 1 | SMPS | In- | IC10 | 17 | 396.08u | 120.11m
Load 1 | SMPS | In- | IC10 | 18 | 396.08u | 180.02m
Load 1 | SMPS | In- | IC10 | 18 | 396.08u | 120.11m
Load 1 | SMPS | In- | IC10 | 32 | 396.08u | 180.02m
Load 1 | SMPS | In- | IC10 | 32 | 396.08u | 120.11m
Load 1 | SMPS | In- | IC10 | 39 | 396.08u | 180.02m
Load 1 | SMPS | In- | IC10 | 39 | 396.08u | 120.11m
Load 2 | SMPS | In+ | U10 | 1 | 5.4969 | 78.308m
Load 2 | SMPS | In+ | U10 | 2 | 5.4968 | 78.273m
Load 2 | SMPS | In+ | U10 | 18 | 5.4966 | 78.118m
Load 2 | SMPS | In- | U10 | 21 | 387.37u | 129m
Load 2 | SMPS | In- | U10 | 21 | 387.37u | 46.94m
Load 2 | SMPS | In- | U10 | 3 | 387.37u | 129m
Load 2 | SMPS | In- | U10 | 3 | 387.37u | 46.94m
Load 2 | SMPS | In- | U10 | 4 | 387.37u | 129m
Load 2 | SMPS | In- | U10 | 4 | 387.37u | 46.94m
Load 2 | SMPS | In- | U10 | 19 | 387.37u | 129m
Load 2 | SMPS | In- | U10 | 19 | 387.37u | 46.94m
Load 2 | SMPS | In- | U10 | 17 | 387.37u | 129m
Load 2 | SMPS | In- | U10 | 17 | 387.37u | 46.94m
Load 3 | Linear | In | IC18 | 6 | 5.4938 | 33.333u
Load 3 | Linear | In | IC18 | 6 | 5.4938 | 77.667m
Load 3 | Linear | In | IC18 | 2 | 5.4938 | 33.333u
Load 3 | Linear | In | IC18 | 2 | 5.4938 | 77.667m
Load 3 | Linear | In | IC18 | 1 | 5.4938 | 33.333u
Load 3 | Linear | In | IC18 | 1 | 5.4938 | 77.667m
Load 3 | Linear | Ref | IC18 | 11 | 1.1435m | 33.334u
Load 3 | Linear | Ref | IC18 | 8 | 1.1436m | 33.334u
Load 3 | Linear | Ref | IC18 | 5 | 1.1477m | 33.332u
Load 4 | Linear | In | IC19 | 1 | 5.4941 | 50u
Load 4 | Linear | In | IC19 | 1 | 5.4941 | 59m
Load 4 | Linear | In | IC19 | 2 | 5.4941 | 50u
Load 4 | Linear | In | IC19 | 2 | 5.4941 | 59m
Load 4 | Linear | Ref | IC19 | 8 | 1.1457m | 50u
Load 4 | Linear | Ref | IC19 | 11 | 1.1459m | 50u

Component Definition Summary:

ID | Ref Des | Type | In+ Pins | In- Pins | Out+ Pins | Out- Pins | S+ | S- | Vout (V) | Efficiency (%) | Ibias (A) | Resistance | Load Current (A) | Vmin | Vmax | Iout max (A) | PD max (W) | Pin Current max (A)
Source 1 | R139, IC11 | SMPS
Load 1 | IC10 | SMPS | IC10-19-21,33 | IC10-13-18,26,32,39 | IC10-5-11 | IC10-13-18,26,32,39 | | | 3.3 | 900m | | | 0 | | | 4 | | 0
Load 2 | U10 | SMPS | U10-1,2,18 | U10-3,4,17,19,21 | U10-5-7,15 | U10-3,4,17,19,21 | | | 1.8 | 900m | | | 0 | | | 1 | | 0
Load 3 | IC18 | Linear | IC18-1,2,6 | IC18-5,8,11 | IC18-9,10 | | | | 3.3 | | 0 | | | | | 500m | 2 | 116.5m
Load 4 | IC19 | Linear | IC19-1,2 | IC19-8,11 | IC19-9,10 | | | | 5 | | 0 | | | | | 200m | 1 | 59m

## Figure <7>: Current density



## Figure <8>: Voltage



Network P1V8 Details



PDN Analysis Pass/Fail: PASS

Power Consumption for This Network: 1.16 Watts

Least Margins:

Margin Type | Absolute | Pass/Fail | ID
Load Voltage (V) | 81.34m | PASS | Load 3
Voltage Source Current (A) | 355m | PASS | Source 1

Margin Type (%) | Percent | Pass/Fail | ID
Load Voltage | 4.76% | PASS | Load 3
Voltage Source Current | 35.50% | PASS | Source 1

Voltage Source Performance Summary:

ID | Source Type | Ref Des | Pass / Fail | Vout setting (V) | Actual Output Voltage (V) | Max Output Current (A) | Actual Output Current (A) | Margin (A) | Margin (%) | Max Pin Current | Highest Actual (A) | Margin (A) | Margin (%) | Max Power Dissipation (W) | Actual Power Dissipation (W) | Margin (W) | Margin (%)
Source 1 | SMPS | U10 | PASS | 1.8 | 1.7994 | 1 | 645m | 355m | 35.50% | 0 | 161.25m | ∞ | ∞

Voltage Source Pin Voltage/Current Details:

ID | SourceType | Terminal | Ref Des | Pin | Max Pin Current (A) | Actual Pin Current (A) | Pass / Fail | Pin Voltage (V)
Source 1 | SMPS | Out+ | U10 | 5 | 0 | 161.25m | PASS | 1.7997
Source 1 | SMPS | Out+ | U10 | 6 | 0 | 161.25m | PASS | 1.7997
Source 1 | SMPS | Out+ | U10 | 15 | 0 | 161.25m | PASS | 1.7997
Source 1 | SMPS | Out+ | U10 | 7 | 0 | 161.25m | PASS | 1.7997
Source 1 | SMPS | Out- | U10 | 21 | 0 | 129m | PASS | 387.37u
Source 1 | SMPS | Out- | U10 | 21 | 0 | 46.94m | PASS | 387.37u
Source 1 | SMPS | Out- | U10 | 3 | 0 | 129m | PASS | 387.37u
Source 1 | SMPS | Out- | U10 | 3 | 0 | 46.94m | PASS | 387.37u
Source 1 | SMPS | Out- | U10 | 4 | 0 | 129m | PASS | 387.37u
Source 1 | SMPS | Out- | U10 | 4 | 0 | 46.94m | PASS | 387.37u
Source 1 | SMPS | Out- | U10 | 19 | 0 | 129m | PASS | 387.37u
Source 1 | SMPS | Out- | U10 | 19 | 0 | 46.94m | PASS | 387.37u
Source 1 | SMPS | Out- | U10 | 17 | 0 | 129m | PASS | 387.37u
Source 1 | SMPS | Out- | U10 | 17 | 0 | 46.94m | PASS | 387.37u

Load Performance Summary:

ID | Load Type | Ref Des | Pass / Fail | Load Value | Min Voltage (V) | Max Voltage (V) | Actual Voltage | Margin (V) | Margin (%) | Min Pwr Pin | Voltage (V) | Max Gnd Pin | Voltage (V) | Actual Current (A)
Load 1 | Current | IC2 | PASS | 40mA | 1.71 | 1.89 | 1.7913 | 81.343m | 4.76% | IC2-34 | 1.7927 | IC2-33 | 1.3853m | 40m
Load 2 | Current | IC6 | PASS | 5mA | 1.71 | 1.89 | 1.7985 | 88.528m | 5.18% | IC6-5 | 1.7993 | IC6-2 | 760.53u | 5m
Load 3 | Current | JB2 | PASS | 500mA | 1.71 | 1.89 | 1.7913 | 81.34m | 4.76% | JB2-2 | 1.7926 | JB2-49 | 1.3077m | 500m
Load 4 | Current | J15, JB3 | PASS | 100mA | 1.71 | 1.89 | 1.7983 | 88.315m | 5.16% | J15-1 | 1.7994 | JB3-55 | 1.1028m | 100m

Load Pin Voltage/Current Details:

ID | Load Type | Terminal | Ref Des | Pin | Pin Voltage (V) | Pin Current (A)
Load 1 | Current | Power | IC2 | 34 | 1.7927 | 40m
Load 1 | Current | Ground | IC2 | 33 | 1.3853m | 40m
Load 2 | Current | Power | IC6 | 5 | 1.7993 | 5m
Load 2 | Current | Ground | IC6 | 11 | 759.78u | 1.6667m
Load 2 | Current | Ground | IC6 | 2 | 760.53u | 1.6666m
Load 2 | Current | Ground | IC6 | 25 | 758.89u | 1.6667m
Load 3 | Current | Power | JB2 | 6 | 1.7927 | 166.69m
Load 3 | Current | Power | JB2 | 4 | 1.7927 | 166.67m
Load 3 | Current | Power | JB2 | 2 | 1.7926 | 166.64m
Load 3 | Current | Ground | JB2 | F1 | 1.1341m | 33.442m
Load 3 | Current | Ground | JB2 | F2 | 976.07u | 33.6m
Load 3 | Current | Ground | JB2 | 60 | 1.2842m | 33.292m
Load 3 | Current | Ground | JB2 | 59 | 1.2934m | 33.283m
Load 3 | Current | Ground | JB2 | 50 | 1.2827m | 33.294m
Load 3 | Current | Ground | JB2 | 49 | 1.3077m | 33.269m
Load 3 | Current | Ground | JB2 | 40 | 1.2796m | 33.297m
Load 3 | Current | Ground | JB2 | 39 | 1.288m | 33.288m
Load 3 | Current | Ground | JB2 | 29 | 1.2937m | 33.283m
Load 3 | Current | Ground | JB2 | 19 | 1.2922m | 33.284m
Load 3 | Current | Ground | JB2 | 69 | 1.2749m | 33.302m
Load 3 | Current | Ground | JB2 | 70 | 1.242m | 33.334m
Load 3 | Current | Ground | JB2 | 79 | 1.2587m | 33.318m
Load 3 | Current | Ground | JB2 | 80 | 1.2435m | 33.333m
Load 3 | Current | Ground | JB2 | 89 | 1.1956m | 33.381m
Load 4 | Current | Power | J15 | 1 | 1.7994 | 100m
Load 4 | Current | Ground | JB3 | F2 | 1.0993m | 5.866m
Load 4 | Current | Ground | JB3 | F1 | 1.0037m | 5.9166m
Load 4 | Current | Ground | JB3 | 5 | 1.0577m | 5.8881m
Load 4 | Current | Ground | JB3 | 6 | 1.0424m | 5.8961m
Load 4 | Current | Ground | JB3 | 11 | 1.056m | 5.8889m
Load 4 | Current | Ground | JB3 | 12 | 1.0386m | 5.8982m
Load 4 | Current | Ground | JB3 | 17 | 1.0769m | 5.8779m
Load 4 | Current | Ground | JB3 | 18 | 1.0582m | 5.8878m
Load 4 | Current | Ground | JB3 | 23 | 1.0701m | 5.8815m
Load 4 | Current | Ground | JB3 | 24 | 1.0543m | 5.8898m
Load 4 | Current | Ground | JB3 | 29 | 1.0861m | 5.873m
Load 4 | Current | Ground | JB3 | 30 | 1.0709m | 5.8811m
Load 4 | Current | Ground | JB3 | 35 | 1.089m | 5.8715m
Load 4 | Current | Ground | JB3 | 36 | 1.0677m | 5.8828m
Load 4 | Current | Ground | JB3 | 45 | 1.0998m | 5.8658m
Load 4 | Current | Ground | JB3 | 46 | 1.0903m | 5.8708m
Load 4 | Current | Ground | JB3 | 55 | 1.1028m | 5.8642m

Component Definition Summary:

ID | Ref Des | Type | In+ Pins | In- Pins | Out+ Pins | Out- Pins | S+ | S- | Vout (V) | Efficiency (%) | Ibias (A) | Resistance | Load Current (A) | Vmin | Vmax | Iout max (A) | PD max (W) | Pin Current max (A)
Source 1 | U10 | SMPS
Load 1 | IC2 | Current | IC2-34 | IC2-33 | | | | | | | | | 40m | 1.71 | 1.89
Load 2 | IC6 | Current | IC6-5 | IC6-2,11,25 | | | | | | | | | 5m | 1.71 | 1.89
Load 3 | JB2 | Current | JB2-2,4,6 | JB2-F1,F2,60,59,50,49,40,39,29,19,69,70,79,80,89 | | | | | | | | | 500m | 1.71 | 1.89
Load 4 | J15, JB3 | Current | J15-1 | JB3-F2,F1,5,6,11,12,17,18,23,24,29,30,35,36,45,46,55 | | | | | | | | | 100m | 1.71 | 1.89

## Figure <9>: Voltage



## Figure <10>: Current density



Network P12V Details



PDN Analysis Pass/Fail: PASS

Power Consumption for This Network: 10.7 Watts

Least Margins:

Margin Type | Absolute | Pass/Fail | ID
Voltage Source Current (A) | 456.08m | PASS | Source 1
Series Element Current (A) | 489.37m | PASS | Series 1

Margin Type (%) | Percent | Pass/Fail | ID
Voltage Source Current | 22.80% | PASS | Source 1
Series Element Current | 48.94% | PASS | Series 1

Voltage Source Performance Summary:

ID | Source Type | Ref Des | Pass / Fail | Vout setting (V) | Actual Output Voltage (V) | Max Output Current (A) | Actual Output Current (A) | Margin (A) | Margin (%) | Max Pin Current | Highest Actual (A) | Margin (A) | Margin (%) | Max Power Dissipation (W) | Actual Power Dissipation (W) | Margin (W) | Margin (%)
Source 1 | Voltage Source | T5, IC12 | PASS | 12 | 11.998 | 2 | 1.5439 | 456.08m | 22.80% | 0 | 771.96m | ∞ | ∞

Voltage Source Pin Voltage/Current Details:

ID | SourceType | Terminal | Ref Des | Pin | Max Pin Current (A) | Actual Pin Current (A) | Pass / Fail | Pin Voltage (V)
Source 1 | Voltage Source | Power | T5 | 3 | 0 | 514.64m | PASS | 11.998
Source 1 | Voltage Source | Power | T5 | 2 | 0 | 514.64m | PASS | 11.998
Source 1 | Voltage Source | Power | T5 | 1 | 0 | 514.64m | PASS | 11.998
Source 1 | Voltage Source | Ground | IC12 | 10 | 0 | 771.96m | PASS | 0
Source 1 | Voltage Source | Ground | IC12 | 7 | 0 | 771.96m | PASS | 0

Load Performance Summary:

ID | Load Type | Ref Des | Pass / Fail | Load Value | Min Voltage (V) | Max Voltage (V) | Actual Voltage | Margin (V) | Margin (%) | Min Pwr Pin | Voltage (V) | Max Gnd Pin | Voltage (V) | Actual Current (A)
Load 1 | SMPS | IC11 | | | | | 11.993 | | | IC11-8 | 11.993 | IC11-9 | 12.03u | 899.42m
Load 2 | SMPS | U9 | | | | | 11.996 | | | U9-B5 | 11.997 | U9-H5 | 582.5u | 133.88m
Load 3 | SMPS | IC22 | | | | | 11.987 | | | IC22-1 | 11.988 | IC22-3 | 1.1795m | 255.31m
Load 4 | SMPS | IC22 | | | | | 11.987 | | | IC22-1 | 11.988 | IC22-3 | 1.1795m | 255.31m

Load Pin Voltage/Current Details:

ID | Load Type | Terminal | Ref Des | Pin | Pin Voltage (V) | Pin Current (A)
Load 1 | SMPS | In+ | IC11 | 8 | 11.993 | 224.93m
Load 1 | SMPS | In+ | IC11 | 8 | 11.993 | 224.93m
Load 1 | SMPS | In+ | IC11 | 8 | 11.993 | 224.76m
Load 1 | SMPS | In+ | IC11 | 8 | 11.993 | 224.8m
Load 1 | SMPS | In- | IC11 | 9 | 12.03u | 1.6669
Load 1 | SMPS | In- | IC11 | 9 | 12.03u | 899.42m
Load 2 | SMPS | In+ | U9 | B5 | 11.997 | 33.468m
Load 2 | SMPS | In+ | U9 | B4 | 11.997 | 33.469m
Load 2 | SMPS | In+ | U9 | A5 | 11.997 | 33.47m
Load 2 | SMPS | In+ | U9 | A4 | 11.997 | 33.47m
Load 2 | SMPS | In- | U9 | H5 | 582.5u | 27.578m
Load 2 | SMPS | In- | U9 | H5 | 582.5u | 14.875m
Load 2 | SMPS | In- | U9 | H4 | 582.5u | 27.578m
Load 2 | SMPS | In- | U9 | H4 | 582.5u | 14.875m
Load 2 | SMPS | In- | U9 | H3 | 582.5u | 27.578m
Load 2 | SMPS | In- | U9 | H3 | 582.5u | 14.875m
Load 2 | SMPS | In- | U9 | G5 | 582.5u | 27.578m
Load 2 | SMPS | In- | U9 | G5 | 582.5u | 14.875m
Load 2 | SMPS | In- | U9 | G4 | 582.5u | 27.578m
Load 2 | SMPS | In- | U9 | G4 | 582.5u | 14.875m
Load 2 | SMPS | In- | U9 | G3 | 582.5u | 27.578m
Load 2 | SMPS | In- | U9 | G3 | 582.5u | 14.875m
Load 2 | SMPS | In- | U9 | F5 | 582.5u | 27.578m
Load 2 | SMPS | In- | U9 | F5 | 582.5u | 14.875m
Load 2 | SMPS | In- | U9 | F4 | 582.5u | 27.578m
Load 2 | SMPS | In- | U9 | F4 | 582.5u | 14.875m
Load 2 | SMPS | In- | U9 | F3 | 582.5u | 27.578m
Load 2 | SMPS | In- | U9 | F3 | 582.5u | 14.875m
Load 3 | SMPS | In+ | IC22 | 1 | 11.988 | 255.31m
Load 3 | SMPS | In- | IC22 | 3 | 1.1795m | 255.31m
Load 4 | SMPS | In+ | IC22 | 1 | 11.988 | 255.31m
Load 4 | SMPS | In- | IC22 | 3 | 1.1795m | 255.31m

Series Element Performance Summary:

ID | Ref Des | Pass / Fail | Voltage (V) | Resistance (Ohms) | Max Current (A) | Actual Current (A) | Margin (A) | Margin (%) | Actual Voltage Drop (V)
Series 1 | L12 | PASS | 0 | 0 | 1 | 510.63m | 489.37m | 48.94% | 0

Series Element Pin Voltage/Current Details:

ID | Terminal | Ref Des | Pin | Pin Voltage (V) | Pin Current (A)
Series 1 | In | L12 | 1 | 11.989 | 510.63m
Series 1 | Out | L12 | 2 | 11.989 | 510.63m

Component Definition Summary:

ID | Ref Des | Type | In+ Pins | In- Pins | Out+ Pins | Out- Pins | S+ | S- | Vout (V) | Efficiency (%) | Ibias (A) | Resistance | Load Current (A) | Vmin | Vmax | Iout max (A) | PD max (W) | Pin Current max (A)
Source 1 | T5, IC12 | Voltage Source | | | T5-1-3 | IC12-7,10 | | | 12 | | | | | | | 2 | | 771.96m
Load 1 | IC11 | SMPS | IC11-8 | IC11-9 | R139-2 | IC11-9 | | | 5.5 | 850m | | | 0 | | | 6 | | 0
Load 2 | U9 | SMPS | U9-B5,B4,A5,A4 | U9-H5,H4,H3,G5,G4,G3,F5,F4,F3 | U9-H2,H1,G2,G1,F2,F1,E5,E4,E3,E2,E1,D5,D4,D3,D2,D1,C2,C1 | U9-H5,H4,H3,G5,G4,G3,F5,F4,F3 | | | -5.5 | 850m | | | 0 | | | 600m | | 0
Load 3 | IC22 | SMPS | IC22-1 | IC22-3 | IC22-7 | IC22-5 | | | 13 | 850m | | | 0 | | | 500m | | 0
Load 4 | IC22 | SMPS | IC22-1 | IC22-3 | IC22-4 | IC22-5 | | | -13 | 850m | | | 0 | | | 500m | | 0
Series 1 | L12 | Series | L12-1 | | L12-2 | | | | 0 | | | 0 | | | | 1 | | 1

## Figure <11>: Current density



## Figure <12>: Voltage



Network P3V3A Details



PDN Analysis Pass/Fail: PASS

Power Consumption for This Network: 769m Watts

Least Margins:

Margin Type | Absolute | Pass/Fail | ID
Load Voltage (V) | 164.06m | PASS | Load 4
Voltage Source Current (A) | 267m | PASS | Source 1
Linear VRM Power Dissipation (W) | 1.4885 | PASS | Source 1

Margin Type (%) | Percent | Pass/Fail | ID
Load Voltage | 5.23% | PASS | Load 4
Voltage Source Current | 53.40% | PASS | Source 1
Linear VRM Power Dissipation | 74.43% | PASS | Source 1

Voltage Source Performance Summary:

ID | Source Type | Ref Des | Pass / Fail | Vout setting (V) | Actual Output Voltage (V) | Max Output Current (A) | Actual Output Current (A) | Margin (A) | Margin (%) | Max Pin Current | Highest Actual (A) | Margin (A) | Margin (%) | Max Power Dissipation (W) | Actual Power Dissipation (W) | Margin (W) | Margin (%)
Source 1 | Linear | IC18 | PASS | 3.3 | 3.3 | 500m | 233m | 267m | 53.40% | 0 | 116.5m | ∞ | ∞ | 2 | 511.46m | 1.4885 | 74.43%

Voltage Source Pin Voltage/Current Details:

ID | SourceType | Terminal | Ref Des | Pin | Max Pin Current (A) | Actual Pin Current (A) | Pass / Fail | Pin Voltage (V)
Source 1 | Linear | Out | IC18 | 10 | 0 | 116.5m | PASS | 3.3011
Source 1 | Linear | Out | IC18 | 9 | 0 | 116.5m | PASS | 3.3011
Source 1 | Linear | Ref | IC18 | 11 | 0 | 33.334u | PASS | 1.1435m
Source 1 | Linear | Ref | IC18 | 8 | 0 | 33.334u | PASS | 1.1436m
Source 1 | Linear | Ref | IC18 | 5 | 0 | 33.332u | PASS | 1.1477m

Load Performance Summary:

ID | Load Type | Ref Des | Pass / Fail | Load Value | Min Voltage (V) | Max Voltage (V) | Actual Voltage | Margin (V) | Margin (%) | Min Pwr Pin | Voltage (V) | Max Gnd Pin | Voltage (V) | Actual Current (A)
Load 1 | Current | U5A | PASS | 18mA | 3.135 | 3.465 | 3.2995 | 164.5m | 5.25% | U5A-2 | 3.3007 | U5A-12 | 1.2077m | 18m
Load 2 | Current | U5B | PASS | 18mA | 3.135 | 3.465 | 3.2995 | 164.52m | 5.25% | U5B-11 | 3.3007 | U5B-9 | 1.2075m | 18m
Load 3 | Current | U6 | PASS | 7mA | 3.135 | 3.465 | 3.2996 | 164.55m | 5.25% | U6-3 | 3.3007 | U6-6 | 1.1447m | 7m
Load 4 | Current | IC20 | PASS | 120mA | 3.135 | 3.465 | 3.2991 | 164.06m | 5.23% | IC20-8 | 3.3003 | IC20-45 | 1.2653m | 120m
Load 5 | Current | U1 | PASS | 70mA | 3.135 | 3.465 | 3.2994 | 164.39m | 5.24% | U1-26 | 3.3006 | U1-6 | 1.1717m | 70m

Load Pin Voltage/Current Details:

ID | Load Type | Terminal | Ref Des | Pin | Pin Voltage (V) | Pin Current (A)
Load 1 | Current | Power | U5A | 2 | 3.3007 | 6.0002m
Load 1 | Current | Power | U5A | 10 | 3.3007 | 5.9999m
Load 1 | Current | Power | U5A | 11 | 3.3007 | 5.9999m
Load 1 | Current | Ground | U5A | 3 | 1.2067m | 4.4999m
Load 1 | Current | Ground | U5A | 9 | 1.2066m | 4.4999m
Load 1 | Current | Ground | U5A | 12 | 1.2077m | 4.4999m
Load 1 | Current | Ground | U5A | 17 | 1.199m | 4.5003m
Load 2 | Current | Power | U5B | 11 | 3.3007 | 6m
Load 2 | Current | Power | U5B | 10 | 3.3007 | 6.0002m
Load 2 | Current | Power | U5B | 2 | 3.3007 | 5.9999m
Load 2 | Current | Ground | U5B | 17 | 1.1939m | 4.5004m
Load 2 | Current | Ground | U5B | 12 | 1.2034m | 4.4999m
Load 2 | Current | Ground | U5B | 9 | 1.2075m | 4.4997m
Load 2 | Current | Ground | U5B | 3 | 1.2015m | 4.5m
Load 3 | Current | Power | U6 | 3 | 3.3007 | 7m
Load 3 | Current | Ground | U6 | 33 | 1.1362m | 1.1669m
Load 3 | Current | Ground | U6 | 29 | 1.1383m | 1.1668m
Load 3 | Current | Ground | U6 | 19 | 1.1397m | 1.1667m
Load 3 | Current | Ground | U6 | 6 | 1.1447m | 1.1665m
Load 3 | Current | Ground | U6 | 5 | 1.1436m | 1.1665m
Load 3 | Current | Ground | U6 | 1 | 1.1409m | 1.1667m
Load 4 | Current | Power | IC20 | 8 | 3.3003 | 59.991m
Load 4 | Current | Power | IC20 | 9 | 3.3003 | 60.009m
Load 4 | Current | Ground | IC20 | 45 | 1.2653m | 120m
Load 5 | Current | Power | U1 | 17 | 3.3006 | 35.008m
Load 5 | Current | Power | U1 | 26 | 3.3006 | 34.993m
Load 5 | Current | Ground | U1 | 6 | 1.1717m | 70m

Component Definition Summary:

ID | Ref Des | Type | In+ Pins | In- Pins | Out+ Pins | Out- Pins | S+ | S- | Vout (V) | Efficiency (%) | Ibias (A) | Resistance | Load Current (A) | Vmin | Vmax | Iout max (A) | PD max (W) | Pin Current max (A)
Source 1 | IC18 | Linear | IC18-1,2,6 | IC18-5,8,11 | IC18-9,10 | | | | 3.3 | | 0 | | | | | 500m | 2
Load 1 | U5A | Current | U5A-2,10,11 | U5A-3,9,12,17 | | | | | | | | | 18m | 3.135 | 3.465
Load 2 | U5B | Current | U5B-2,10,11 | U5B-3,9,12,17 | | | | | | | | | 18m | 3.135 | 3.465
Load 3 | U6 | Current | U6-3 | U6-1,5,6,19,29,33 | | | | | | | | | 7m | 3.135 | 3.465
Load 4 | IC20 | Current | IC20-8,9 | IC20-45 | | | | | | | | | 120m | 3.135 | 3.465
Load 5 | U1 | Current | U1-17,26 | U1-6 | | | | | | | | | 70m | 3.135 | 3.465

## Figure <13>: Current density



## Figure <14>: Voltage



Network P5V0A Details



PDN Analysis Pass/Fail: PASS

Power Consumption for This Network: 590m Watts

Least Margins:

Margin Type | Absolute | Pass/Fail | ID
Load Voltage (V) | 249.14m | PASS | Load 2
Voltage Source Current (A) | 82m | PASS | Source 1
Linear VRM Power Dissipation (W) | 941.28m | PASS | Source 1

Margin Type (%) | Percent | Pass/Fail | ID
Load Voltage | 5.24% | PASS | Load 2
Voltage Source Current | 41.00% | PASS | Source 1
Linear VRM Power Dissipation | 94.13% | PASS | Source 1

Voltage Source Performance Summary:

ID | Source Type | Ref Des | Pass / Fail | Vout setting (V) | Actual Output Voltage (V) | Max Output Current (A) | Actual Output Current (A) | Margin (A) | Margin (%) | Max Pin Current | Highest Actual (A) | Margin (A) | Margin (%) | Max Power Dissipation (W) | Actual Power Dissipation (W) | Margin (W) | Margin (%)
Source 1 | Linear | IC19 | PASS | 5 | 5 | 200m | 118m | 82m | 41.00% | 0 | 59m | ∞ | ∞ | 1 | 58.72m | 941.28m | 94.13%

Voltage Source Pin Voltage/Current Details:

ID | SourceType | Terminal | Ref Des | Pin | Max Pin Current (A) | Actual Pin Current (A) | Pass / Fail | Pin Voltage (V)
Source 1 | Linear | Out | IC19 | 9 | 0 | 59m | PASS | 5.0011
Source 1 | Linear | Out | IC19 | 10 | 0 | 59m | PASS | 5.0011
Source 1 | Linear | Ref | IC19 | 8 | 0 | 50u | PASS | 1.1457m
Source 1 | Linear | Ref | IC19 | 11 | 0 | 50u | PASS | 1.1459m

Load Performance Summary:

ID | Load Type | Ref Des | Pass / Fail | Load Value | Min Voltage (V) | Max Voltage (V) | Actual Voltage | Margin (V) | Margin (%) | Min Pwr Pin | Voltage (V) | Max Gnd Pin | Voltage (V) | Actual Current (A)
Load 1 | Current | U4A | PASS | 59mA | 4.75 | 5.25 | 4.9992 | 249.16m | 5.25% | U4A-6 | 5.0003 | U4A-17 | 1.1698m | 59m
Load 2 | Current | U4B | PASS | 59mA | 4.75 | 5.25 | 4.9991 | 249.14m | 5.24% | U4B-6 | 5.0003 | U4B-17 | 1.1616m | 59m

Load Pin Voltage/Current Details:

ID | Load Type | Terminal | Ref Des | Pin | Pin Voltage (V) | Pin Current (A)
Load 1 | Current | Power | U4A | 6 | 5.0003 | 59m
Load 1 | Current | Ground | U4A | 17 | 1.1698m | 59m
Load 2 | Current | Power | U4B | 6 | 5.0003 | 59m
Load 2 | Current | Ground | U4B | 17 | 1.1616m | 59m

Component Definition Summary:

ID | Ref Des | Type | In+ Pins | In- Pins | Out+ Pins | Out- Pins | S+ | S- | Vout (V) | Efficiency (%) | Ibias (A) | Resistance | Load Current (A) | Vmin | Vmax | Iout max (A) | PD max (W) | Pin Current max (A)
Source 1 | IC19 | Linear | IC19-1,2 | IC19-8,11 | IC19-9,10 | | | | 5 | | 0 | | | | | 200m | 1
Load 1 | U4A | Current | U4A-6 | U4A-17 | | | | | | | | | 59m | 4.75 | 5.25
Load 2 | U4B | Current | U4B-6 | U4B-17 | | | | | | | | | 59m | 4.75 | 5.25

## Figure <15>: Current density



## Figure <16>: Voltage



Network N2V5A Details



PDN Analysis Pass/Fail: PASS

Power Consumption for This Network: 325m Watts

Least Margins:

Margin Type | Absolute | Pass/Fail | ID
Load Voltage (V) | 124.25m | PASS | Load 1
Voltage Source Current (A) | 70m | PASS | Source 1
Linear VRM Power Dissipation (W) | 610.01m | PASS | Source 1

Margin Type (%) | Percent | Pass/Fail | ID
Load Voltage | 5.23% | PASS | Load 1
Voltage Source Current | 35.00% | PASS | Source 1
Linear VRM Power Dissipation | 61.00% | PASS | Source 1

Voltage Source Performance Summary:

ID | Source Type | Ref Des | Pass / Fail | Vout setting (V) | Actual Output Voltage (V) | Max Output Current (A) | Actual Output Current (A) | Margin (A) | Margin (%) | Max Pin Current | Highest Actual (A) | Margin (A) | Margin (%) | Max Power Dissipation (W) | Actual Power Dissipation (W) | Margin (W) | Margin (%)
Source 1 | Linear | IC8 | PASS | -2.5 | 2.5 | 200m | 130m | 70m | 35.00% | 0 | 130m | ∞ | ∞ | 1 | 389.99m | 610.01m | 61.00%

Voltage Source Pin Voltage/Current Details:

ID | SourceType | Terminal | Ref Des | Pin | Max Pin Current (A) | Actual Pin Current (A) | Pass / Fail | Pin Voltage (V)
Source 1 | Linear | Out | IC8 | 5 | 0 | 130m | PASS | -2.4989
Source 1 | Linear | Ref | IC8 | 1 | 0 | 100u | PASS | 1.1342m

Load Performance Summary:

ID | Load Type | Ref Des | Pass / Fail | Load Value | Min Voltage (V) | Max Voltage (V) | Actual Voltage | Margin (V) | Margin (%) | Min Pwr Pin | Voltage (V) | Max Gnd Pin | Voltage (V) | Actual Current (A)
Load 1 | Current | IC3 | PASS | 130mA | 2.375 | 2.625 | 2.4992 | 124.25m | 5.23% | IC3-22 | -2.4981 | IC3-25 | 1.1054m | 130m

Load Pin Voltage/Current Details:

ID | Load Type | Terminal | Ref Des | Pin | Pin Voltage (V) | Pin Current (A)
Load 1 | Current | Power | IC3 | 22 | -2.4981 | 32.499m
Load 1 | Current | Power | IC3 | 21 | -2.4981 | 32.498m
Load 1 | Current | Power | IC3 | 16 | -2.4981 | 32.495m
Load 1 | Current | Power | IC3 | 15 | -2.4982 | 32.509m
Load 1 | Current | Ground | IC3 | 25 | 1.1054m | 130m

Component Definition Summary:

ID | Ref Des | Type | In+ Pins | In- Pins | Out+ Pins | Out- Pins | S+ | S- | Vout (V) | Efficiency (%) | Ibias (A) | Resistance | Load Current (A) | Vmin | Vmax | Iout max (A) | PD max (W) | Pin Current max (A)
Source 1 | IC8 | Linear | IC8-2 | IC8-1 | IC8-5 | | | | -2.5 | | 0 | | | | | 200m | 1
Load 1 | IC3 | Current | IC3-15,16,21,22 | IC3-25 | | | | | | | | | 130m | 2.375 | 2.625

## Figure <17>: Current density



## Figure <18>: Voltage



Network N5V0A Details



PDN Analysis Pass/Fail: PASS

Power Consumption for This Network: 590m Watts

Least Margins:

Margin Type | Absolute | Pass/Fail | ID
Load Voltage (V) | 249.51m | PASS | Load 1
Voltage Source Current (A) | 82m | PASS | Source 1
Linear VRM Power Dissipation (W) | 940.97m | PASS | Source 1

Margin Type (%) | Percent | Pass/Fail | ID
Load Voltage | 5.25% | PASS | Load 1
Voltage Source Current | 41.00% | PASS | Source 1
Linear VRM Power Dissipation | 94.10% | PASS | Source 1

Voltage Source Performance Summary:

ID | Source Type | Ref Des | Pass / Fail | Vout setting (V) | Actual Output Voltage (V) | Max Output Current (A) | Actual Output Current (A) | Margin (A) | Margin (%) | Max Pin Current | Highest Actual (A) | Margin (A) | Margin (%) | Max Power Dissipation (W) | Actual Power Dissipation (W) | Margin (W) | Margin (%)
Source 1 | Linear | IC17 | PASS | -5 | 5 | 200m | 118m | 82m | 41.00% | 0 | 118m | ∞ | ∞ | 1 | 59.029m | 940.97m | 94.10%

Voltage Source Pin Voltage/Current Details:

ID | SourceType | Terminal | Ref Des | Pin | Max Pin Current (A) | Actual Pin Current (A) | Pass / Fail | Pin Voltage (V)
Source 1 | Linear | Out | IC17 | 5 | 0 | 118m | PASS | -4.9989
Source 1 | Linear | Ref | IC17 | 1 | 0 | 100u | PASS | 1.136m

Load Performance Summary:

ID | Load Type | Ref Des | Pass / Fail | Load Value | Min Voltage (V) | Max Voltage (V) | Actual Voltage | Margin (V) | Margin (%) | Min Pwr Pin | Voltage (V) | Max Gnd Pin | Voltage (V) | Actual Current (A)
Load 1 | Current | U4A | PASS | 59mA | 4.75 | 5.25 | 4.9995 | 249.51m | 5.25% | U4A-4 | -4.9983 | U4A-17 | 1.1698m | 59m
Load 2 | Current | U4B | PASS | 59mA | 4.75 | 5.25 | 4.9995 | 249.53m | 5.25% | U4B-4 | -4.9984 | U4B-17 | 1.1616m | 59m

Load Pin Voltage/Current Details:

ID | Load Type | Terminal | Ref Des | Pin | Pin Voltage (V) | Pin Current (A)
Load 1 | Current | Power | U4A | 12 | -4.9984 | 29.505m
Load 1 | Current | Power | U4A | 4 | -4.9983 | 29.495m
Load 1 | Current | Ground | U4A | 17 | 1.1698m | 59m
Load 2 | Current | Power | U4B | 12 | -4.9985 | 29.517m
Load 2 | Current | Power | U4B | 4 | -4.9984 | 29.483m
Load 2 | Current | Ground | U4B | 17 | 1.1616m | 59m

Component Definition Summary:

ID | Ref Des | Type | In+ Pins | In- Pins | Out+ Pins | Out- Pins | S+ | S- | Vout (V) | Efficiency (%) | Ibias (A) | Resistance | Load Current (A) | Vmin | Vmax | Iout max (A) | PD max (W) | Pin Current max (A)
Source 1 | IC17 | Linear | IC17-2 | IC17-1 | IC17-5 | | | | -5 | | 0 | | | | | 200m | 1
Load 1 | U4A | Current | U4A-4,12 | U4A-17 | | | | | | | | | 59m | 4.75 | 5.25
Load 2 | U4B | Current | U4B-4,12 | U4B-17 | | | | | | | | | 59m | 4.75 | 5.25

## Figure <19>: Current density 029



## Figure <20>: Voltage



Network N5V5 Details



PDN Analysis Pass/Fail: PASS

Power Consumption for This Network: 450m Watts

Least Margins:

Margin Type | Absolute | Pass/Fail | ID
Voltage Source Current (A) | 351.8m | PASS | Source 1

Margin Type (%) | Percent | Pass/Fail | ID
Voltage Source Current | 58.63% | PASS | Source 1

Voltage Source Performance Summary:

ID | Source Type | Ref Des | Pass / Fail | Vout setting (V) | Actual Output Voltage (V) | Max Output Current (A) | Actual Output Current (A) | Margin (A) | Margin (%) | Max Pin Current | Highest Actual (A) | Margin (A) | Margin (%) | Max Power Dissipation (W) | Actual Power Dissipation (W) | Margin (W) | Margin (%)
Source 1 | SMPS | U9 | PASS | -5.5 | 5.4998 | 600m | 248.2m | 351.8m | 58.63% | 0 | 33.47m | ∞ | ∞

Voltage Source Pin Voltage/Current Details:

ID | SourceType | Terminal | Ref Des | Pin | Max Pin Current (A) | Actual Pin Current (A) | Pass / Fail | Pin Voltage (V)
Source 1 | SMPS | Out+ | U9 | H2 | 0 | 13.789m | PASS | -5.4992
Source 1 | SMPS | Out+ | U9 | H1 | 0 | 13.789m | PASS | -5.4992
Source 1 | SMPS | Out+ | U9 | G2 | 0 | 13.789m | PASS | -5.4992
Source 1 | SMPS | Out+ | U9 | G1 | 0 | 13.789m | PASS | -5.4992
Source 1 | SMPS | Out+ | U9 | F2 | 0 | 13.789m | PASS | -5.4992
Source 1 | SMPS | Out+ | U9 | F1 | 0 | 13.789m | PASS | -5.4992
Source 1 | SMPS | Out+ | U9 | E5 | 0 | 13.789m | PASS | -5.4992
Source 1 | SMPS | Out+ | U9 | E4 | 0 | 13.789m | PASS | -5.4992
Source 1 | SMPS | Out+ | U9 | E3 | 0 | 13.789m | PASS | -5.4992
Source 1 | SMPS | Out+ | U9 | E2 | 0 | 13.789m | PASS | -5.4992
Source 1 | SMPS | Out+ | U9 | E1 | 0 | 13.789m | PASS | -5.4992
Source 1 | SMPS | Out+ | U9 | D5 | 0 | 13.789m | PASS | -5.4992
Source 1 | SMPS | Out+ | U9 | D4 | 0 | 13.789m | PASS | -5.4992
Source 1 | SMPS | Out+ | U9 | D3 | 0 | 13.789m | PASS | -5.4992
Source 1 | SMPS | Out+ | U9 | D2 | 0 | 13.789m | PASS | -5.4992
Source 1 | SMPS | Out+ | U9 | D1 | 0 | 13.789m | PASS | -5.4992
Source 1 | SMPS | Out+ | U9 | C2 | 0 | 13.789m | PASS | -5.4992
Source 1 | SMPS | Out+ | U9 | C1 | 0 | 13.789m | PASS | -5.4992
Source 1 | SMPS | Out- | U9 | H5 | 0 | 27.578m | PASS | 582.5u
Source 1 | SMPS | Out- | U9 | H5 | 0 | 14.875m | PASS | 582.5u
Source 1 | SMPS | Out- | U9 | H4 | 0 | 27.578m | PASS | 582.5u
Source 1 | SMPS | Out- | U9 | H4 | 0 | 14.875m | PASS | 582.5u
Source 1 | SMPS | Out- | U9 | H3 | 0 | 27.578m | PASS | 582.5u
Source 1 | SMPS | Out- | U9 | H3 | 0 | 14.875m | PASS | 582.5u
Source 1 | SMPS | Out- | U9 | G5 | 0 | 27.578m | PASS | 582.5u
Source 1 | SMPS | Out- | U9 | G5 | 0 | 14.875m | PASS | 582.5u
Source 1 | SMPS | Out- | U9 | G4 | 0 | 27.578m | PASS | 582.5u
Source 1 | SMPS | Out- | U9 | G4 | 0 | 14.875m | PASS | 582.5u
Source 1 | SMPS | Out- | U9 | G3 | 0 | 27.578m | PASS | 582.5u
Source 1 | SMPS | Out- | U9 | G3 | 0 | 14.875m | PASS | 582.5u
Source 1 | SMPS | Out- | U9 | F5 | 0 | 27.578m | PASS | 582.5u
Source 1 | SMPS | Out- | U9 | F5 | 0 | 14.875m | PASS | 582.5u
Source 1 | SMPS | Out- | U9 | F4 | 0 | 27.578m | PASS | 582.5u
Source 1 | SMPS | Out- | U9 | F4 | 0 | 14.875m | PASS | 582.5u
Source 1 | SMPS | Out- | U9 | F3 | 0 | 27.578m | PASS | 582.5u
Source 1 | SMPS | Out- | U9 | F3 | 0 | 14.875m | PASS | 582.5u

Load Performance Summary:

ID | Load Type | Ref Des | Pass / Fail | Load Value | Min Voltage (V) | Max Voltage (V) | Actual Voltage | Margin (V) | Margin (%) | Min Pwr Pin | Voltage (V) | Max Gnd Pin | Voltage (V) | Actual Current (A)
Load 1 | Linear | IC17 | | | | | 5.4956 | | | IC17-2 | -5.4945 | IC17-1 | 1.136m | 118.1m
Load 2 | Linear | IC8 | | | | | 5.4957 | | | IC8-2 | -5.4945 | IC8-1 | 1.1342m | 130.1m

Load Pin Voltage/Current Details:

ID | Load Type | Terminal | Ref Des | Pin | Pin Voltage (V) | Pin Current (A)
Load 1 | Linear | In | IC17 | 2 | -5.4945 | 100u
Load 1 | Linear | In | IC17 | 2 | -5.4945 | 118m
Load 1 | Linear | Ref | IC17 | 1 | 1.136m | 100u
Load 2 | Linear | In | IC8 | 2 | -5.4945 | 100u
Load 2 | Linear | In | IC8 | 2 | -5.4945 | 130m
Load 2 | Linear | Ref | IC8 | 1 | 1.1342m | 100u

Component Definition Summary:

ID | Ref Des | Type | In+ Pins | In- Pins | Out+ Pins | Out- Pins | S+ | S- | Vout (V) | Efficiency (%) | Ibias (A) | Resistance | Load Current (A) | Vmin | Vmax | Iout max (A) | PD max (W) | Pin Current max (A)
Source 1 | U9 | SMPS
Load 1 | IC17 | Linear | IC17-2 | IC17-1 | IC17-5 | | | | -5 | | 0 | | | | | 200m | 1 | 118m
Load 2 | IC8 | Linear | IC8-2 | IC8-1 | IC8-5 | | | | -2.5 | | 0 | | | | | 200m | 1 | 130m

## Figure <21>: Current density



## Figure <22>: Voltage



Network P13V0S Details



PDN Analysis Pass/Fail: PASS

Power Consumption for This Network: 201m Watts

Least Margins:

Margin Type | Absolute | Pass/Fail | ID
Voltage Source Current (A) | 299.9m | PASS | Source 1
Series Element Current (A) | 799.9m | PASS | Series 1

Margin Type (%) | Percent | Pass/Fail | ID
Voltage Source Current | 59.98% | PASS | Source 1
Series Element Current | 79.99% | PASS | Series 1

Voltage Source Performance Summary:

ID | Source Type | Ref Des | Pass / Fail | Vout setting (V) | Actual Output Voltage (V) | Max Output Current (A) | Actual Output Current (A) | Margin (A) | Margin (%) | Max Pin Current | Highest Actual (A) | Margin (A) | Margin (%) | Max Power Dissipation (W) | Actual Power Dissipation (W) | Margin (W) | Margin (%)
Source 1 | SMPS | IC22 | PASS | 13 | 13 | 500m | 200.1m | 299.9m | 59.98% | 0 | 255.31m | ∞ | ∞

Voltage Source Pin Voltage/Current Details:

ID | SourceType | Terminal | Ref Des | Pin | Max Pin Current (A) | Actual Pin Current (A) | Pass / Fail | Pin Voltage (V)
Source 1 | SMPS | Out+ | IC22 | 7 | 0 | 200.1m | PASS | 13.001
Source 1 | SMPS | Out- | IC22 | 5 | 0 | 200.1m | PASS | 1.0481m

Load Performance Summary:

ID | Load Type | Ref Des | Pass / Fail | Load Value | Min Voltage (V) | Max Voltage (V) | Actual Voltage | Margin (V) | Margin (%) | Min Pwr Pin | Voltage (V) | Max Gnd Pin | Voltage (V) | Actual Current (A)
Load 1 | Linear | IC21 | | | | | 12.999 | | | IC21-2 | 13 | IC21-5 | 1.1107m | 200.1m

Load Pin Voltage/Current Details:

ID | Load Type | Terminal | Ref Des | Pin | Pin Voltage (V) | Pin Current (A)
Load 1 | Linear | In | IC21 | 2 | 13 | 50u
Load 1 | Linear | In | IC21 | 2 | 13 | 100m
Load 1 | Linear | In | IC21 | 1 | 13 | 50u
Load 1 | Linear | In | IC21 | 1 | 13 | 100m
Load 1 | Linear | Ref | IC21 | 11 | 1.1047m | 33.334u
Load 1 | Linear | Ref | IC21 | 8 | 1.1046m | 33.334u
Load 1 | Linear | Ref | IC21 | 5 | 1.1107m | 33.331u

Series Element Performance Summary:

ID | Ref Des | Pass / Fail | Voltage (V) | Resistance (Ohms) | Max Current (A) | Actual Current (A) | Margin (A) | Margin (%) | Actual Voltage Drop (V)
Series 1 | L10 | PASS | 0 | 0 | 1 | 200.1m | 799.9m | 79.99% | 0
Series 2 | L11 | PASS | 0 | 0 | 1 | 200.1m | 799.9m | 79.99% | 0

Series Element Pin Voltage/Current Details:

ID | Terminal | Ref Des | Pin | Pin Voltage (V) | Pin Current (A)
Series 1 | In | L10 | 1 | 13.001 | 200.1m
Series 1 | Out | L10 | 2 | 13.001 | 200.1m
Series 2 | In | L11 | 1 | 13.001 | 200.1m
Series 2 | Out | L11 | 2 | 13.001 | 200.1m

Component Definition Summary:

ID | Ref Des | Type | In+ Pins | In- Pins | Out+ Pins | Out- Pins | S+ | S- | Vout (V) | Efficiency (%) | Ibias (A) | Resistance | Load Current (A) | Vmin | Vmax | Iout max (A) | PD max (W) | Pin Current max (A)
Source 1 | IC22 | SMPS
Load 1 | IC21 | Linear | IC21-1,2 | IC21-5,8,11 | IC21-9,10 | | | | 12 | | 0 | | | | | 200m | 1 | 100m
Series 1 | L10 | Series | L10-1 | | L10-2 | | | | 0 | | | 0 | | | | 1 | | 1
Series 2 | L11 | Series | L11-1 | | L11-2 | | | | 0 | | | 0 | | | | 1 | | 1

## Figure <23>: Current density



## Figure <24>: Voltage



Network P12V0A Details



PDN Analysis Pass/Fail: PASS

Power Consumption for This Network: 2.4 Watts

Least Margins:

Margin Type | Absolute | Pass/Fail | ID
Load Voltage (V) | 594.42m | PASS | Load 1
Voltage Source Current (A) | 0 | PASS | Source 1
Linear VRM Power Dissipation (W) | 798.9m | PASS | Source 1

Margin Type (%) | Percent | Pass/Fail | ID
Load Voltage | 5.21% | PASS | Load 1
Voltage Source Current | ∞ | PASS | Source 1
Linear VRM Power Dissipation | 79.89% | PASS | Source 1

Voltage Source Performance Summary:

ID | Source Type | Ref Des | Pass / Fail | Vout setting (V) | Actual Output Voltage (V) | Max Output Current (A) | Actual Output Current (A) | Margin (A) | Margin (%) | Max Pin Current | Highest Actual (A) | Margin (A) | Margin (%) | Max Power Dissipation (W) | Actual Power Dissipation (W) | Margin (W) | Margin (%)
Source 1 | Linear | IC21 | PASS | 12 | 12 | 200m | 200m | 0 | ∞ | 0 | 100m | ∞ | ∞ | 1 | 201.1m | 798.9m | 79.89%

Voltage Source Pin Voltage/Current Details:

ID | SourceType | Terminal | Ref Des | Pin | Max Pin Current (A) | Actual Pin Current (A) | Pass / Fail | Pin Voltage (V)
Source 1 | Linear | Out | IC21 | 10 | 0 | 100m | PASS | 12.001
Source 1 | Linear | Out | IC21 | 9 | 0 | 100m | PASS | 12.001
Source 1 | Linear | Ref | IC21 | 11 | 0 | 33.334u | PASS | 1.1047m
Source 1 | Linear | Ref | IC21 | 8 | 0 | 33.334u | PASS | 1.1046m
Source 1 | Linear | Ref | IC21 | 5 | 0 | 33.331u | PASS | 1.1107m

Load Performance Summary:

ID | Load Type | Ref Des | Pass / Fail | Load Value | Min Voltage (V) | Max Voltage (V) | Actual Voltage | Margin (V) | Margin (%) | Min Pwr Pin | Voltage (V) | Max Gnd Pin | Voltage (V) | Actual Current (A)
Load 1 | Current | J16 | PASS | 100mA | 11.4 | 12.6 | 11.994 | 594.42m | 5.21% | J16-15 | 11.996 | J16-1 | 1.1315m | 100m
Load 2 | Current | J3 | PASS | 100mA | 11.4 | 12.6 | 11.998 | 597.58m | 5.24% | J3-25 | 11.999 | J3-20 | 1.1699m | 100m

Load Pin Voltage/Current Details:

ID | Load Type | Terminal | Ref Des | Pin | Pin Voltage (V) | Pin Current (A)
Load 1 | Current | Power | J16 | 15 | 11.996 | 100m
Load 1 | Current | Ground | J16 | 13 | 1.1114m | 20.007m
Load 1 | Current | Ground | J16 | 1 | 1.1315m | 19.995m
Load 1 | Current | Ground | J16 | 4 | 1.1303m | 19.996m
Load 1 | Current | Ground | J16 | 7 | 1.1226m | 20m
Load 1 | Current | Ground | J16 | 10 | 1.1189m | 20.002m
Load 2 | Current | Power | J3 | 25 | 11.999 | 100m
Load 2 | Current | Ground | J3 | 21 | 1.1582m | 6.2458m
Load 2 | Current | Ground | J3 | 23 | 1.158m | 6.246m
Load 2 | Current | Ground | J3 | 24 | 1.1689m | 6.2401m
Load 2 | Current | Ground | J3 | 11 | 1.1465m | 6.2521m
Load 2 | Current | Ground | J3 | 12 | 1.1547m | 6.2477m
Load 2 | Current | Ground | J3 | 14 | 1.1606m | 6.2446m
Load 2 | Current | Ground | J3 | 15 | 1.1541m | 6.248m
Load 2 | Current | Ground | J3 | 18 | 1.1685m | 6.2404m
Load 2 | Current | Ground | J3 | 17 | 1.1572m | 6.2464m
Load 2 | Current | Ground | J3 | 20 | 1.1699m | 6.2396m
Load 2 | Current | Ground | J3 | 2 | 1.1281m | 6.2618m
Load 2 | Current | Ground | J3 | 3 | 1.1271m | 6.2624m
Load 2 | Current | Ground | J3 | 6 | 1.1379m | 6.2566m
Load 2 | Current | Ground | J3 | 5 | 1.1311m | 6.2602m
Load 2 | Current | Ground | J3 | 8 | 1.1438m | 6.2535m
Load 2 | Current | Ground | J3 | 9 | 1.1409m | 6.255m

Component Definition Summary:

ID | Ref Des | Type | In+ Pins | In- Pins | Out+ Pins | Out- Pins | S+ | S- | Vout (V) | Efficiency (%) | Ibias (A) | Resistance | Load Current (A) | Vmin | Vmax | Iout max (A) | PD max (W) | Pin Current max (A)
Source 1 | IC21 | Linear | IC21-1,2 | IC21-5,8,11 | IC21-9,10 | | | | 12 | | 0 | | | | | 200m | 1
Load 1 | J16 | Current | J16-15 | J16-1,4,7,10,13 | | | | | | | | | 100m | 11.4 | 12.6
Load 2 | J3 | Current | J3-25 | J3-2,3,5,6,8,9,11,12,14,15,17,18,20,21,23,24 | | | | | | | | | 100m | 11.4 | 12.6

## Figure <25>: Current density



## Figure <26>: Voltage



Network N13V0S Details



PDN Analysis Pass/Fail: PASS

Power Consumption for This Network: 201m Watts

Least Margins:

Margin Type | Absolute | Pass/Fail | ID
Voltage Source Current (A) | 299.9m | PASS | Source 1
Series Element Current (A) | 799.9m | PASS | Series 1

Margin Type (%) | Percent | Pass/Fail | ID
Voltage Source Current | 59.98% | PASS | Source 1
Series Element Current | 79.99% | PASS | Series 1

Voltage Source Performance Summary:

ID | Source Type | Ref Des | Pass / Fail | Vout setting (V) | Actual Output Voltage (V) | Max Output Current (A) | Actual Output Current (A) | Margin (A) | Margin (%) | Max Pin Current | Highest Actual (A) | Margin (A) | Margin (%) | Max Power Dissipation (W) | Actual Power Dissipation (W) | Margin (W) | Margin (%)
Source 1 | SMPS | IC22 | PASS | -13 | 13 | 500m | 200.1m | 299.9m | 59.98% | 0 | 255.31m | ∞ | ∞

Voltage Source Pin Voltage/Current Details:

ID | SourceType | Terminal | Ref Des | Pin | Max Pin Current (A) | Actual Pin Current (A) | Pass / Fail | Pin Voltage (V)
Source 1 | SMPS | Out+ | IC22 | 4 | 0 | 200.1m | PASS | -12.999
Source 1 | SMPS | Out- | IC22 | 5 | 0 | 200.1m | PASS | 1.0481m

Load Performance Summary:

ID | Load Type | Ref Des | Pass / Fail | Load Value | Min Voltage (V) | Max Voltage (V) | Actual Voltage | Margin (V) | Margin (%) | Min Pwr Pin | Voltage (V) | Max Gnd Pin | Voltage (V) | Actual Current (A)
Load 1 | Linear | IC23 | | | | | 12.999 | | | IC23-2 | -12.998 | IC23-1 | 1.0518m | 200.1m

Load Pin Voltage/Current Details:

ID | Load Type | Terminal | Ref Des | Pin | Pin Voltage (V) | Pin Current (A)
Load 1 | Linear | In | IC23 | 2 | -12.998 | 100u
Load 1 | Linear | In | IC23 | 2 | -12.998 | 200m
Load 1 | Linear | Ref | IC23 | 1 | 1.0518m | 100u

Series Element Performance Summary:

ID | Ref Des | Pass / Fail | Voltage (V) | Resistance (Ohms) | Max Current (A) | Actual Current (A) | Margin (A) | Margin (%) | Actual Voltage Drop (V)
Series 1 | L13 | PASS | 0 | 0 | 1 | 200.1m | 799.9m | 79.99% | 0
Series 2 | L14 | PASS | 0 | 0 | 1 | 200.1m | 799.9m | 79.99% | 0

Series Element Pin Voltage/Current Details:

ID | Terminal | Ref Des | Pin | Pin Voltage (V) | Pin Current (A)
Series 1 | In | L13 | 1 | -12.999 | 200.1m
Series 1 | Out | L13 | 2 | -12.999 | 200.1m
Series 2 | In | L14 | 1 | -12.998 | 200.1m
Series 2 | Out | L14 | 2 | -12.998 | 200.1m

Component Definition Summary:

ID | Ref Des | Type | In+ Pins | In- Pins | Out+ Pins | Out- Pins | S+ | S- | Vout (V) | Efficiency (%) | Ibias (A) | Resistance | Load Current (A) | Vmin | Vmax | Iout max (A) | PD max (W) | Pin Current max (A)
Source 1 | IC22 | SMPS
Load 1 | IC23 | Linear | IC23-2 | IC23-1 | IC23-5 | | | | -12 | | 0 | | | | | 200m | 1 | 200m
Series 1 | L13 | Series | L13-1 | | L13-2 | | | | 0 | | | 0 | | | | 1 | | 1
Series 2 | L14 | Series | L14-1 | | L14-2 | | | | 0 | | | 0 | | | | 1 | | 1

## Figure <27>: Current density



## Figure <28>: Screenshot 039



Network N12V0A Details



PDN Analysis Pass/Fail: PASS

Power Consumption for This Network: 2.4 Watts

Least Margins:

Margin Type | Absolute | Pass/Fail | ID
Load Voltage (V) | 595.56m | PASS | Load 2
Voltage Source Current (A) | 0 | PASS | Source 1
Linear VRM Power Dissipation (W) | 798.92m | PASS | Source 1

Margin Type (%) | Percent | Pass/Fail | ID
Load Voltage | 5.22% | PASS | Load 2
Voltage Source Current | ∞ | PASS | Source 1
Linear VRM Power Dissipation | 79.89% | PASS | Source 1

Voltage Source Performance Summary:

ID | Source Type | Ref Des | Pass / Fail | Vout setting (V) | Actual Output Voltage (V) | Max Output Current (A) | Actual Output Current (A) | Margin (A) | Margin (%) | Max Pin Current | Highest Actual (A) | Margin (A) | Margin (%) | Max Power Dissipation (W) | Actual Power Dissipation (W) | Margin (W) | Margin (%)
Source 1 | Linear | IC23 | PASS | -12 | 12 | 200m | 200m | 0 | ∞ | 0 | 200m | ∞ | ∞ | 1 | 201.08m | 798.92m | 79.89%

Voltage Source Pin Voltage/Current Details:

ID | SourceType | Terminal | Ref Des | Pin | Max Pin Current (A) | Actual Pin Current (A) | Pass / Fail | Pin Voltage (V)
Source 1 | Linear | Out | IC23 | 5 | 0 | 200m | PASS | -11.999
Source 1 | Linear | Ref | IC23 | 1 | 0 | 100u | PASS | 1.0518m

Load Performance Summary:

ID | Load Type | Ref Des | Pass / Fail | Load Value | Min Voltage (V) | Max Voltage (V) | Actual Voltage | Margin (V) | Margin (%) | Min Pwr Pin | Voltage (V) | Max Gnd Pin | Voltage (V) | Actual Current (A)
Load 1 | Current | J3 | PASS | 100mA | 11.4 | 12.6 | 11.998 | 597.78m | 5.24% | J3-26 | -11.997 | J3-3 | 1.1271m | 100m
Load 2 | Current | J16 | PASS | 100mA | 11.4 | 12.6 | 11.996 | 595.56m | 5.22% | J16-16 | -11.994 | J16-13 | 1.1114m | 100m

Load Pin Voltage/Current Details:

ID | Load Type | Terminal | Ref Des | Pin | Pin Voltage (V) | Pin Current (A)
Load 1 | Current | Power | J3 | 26 | -11.997 | 100m
Load 1 | Current | Ground | J3 | 21 | 1.1582m | 6.2542m
Load 1 | Current | Ground | J3 | 23 | 1.158m | 6.2541m
Load 1 | Current | Ground | J3 | 24 | 1.1689m | 6.2599m
Load 1 | Current | Ground | J3 | 11 | 1.1465m | 6.248m
Load 1 | Current | Ground | J3 | 12 | 1.1547m | 6.2523m
Load 1 | Current | Ground | J3 | 14 | 1.1606m | 6.2555m
Load 1 | Current | Ground | J3 | 15 | 1.1541m | 6.252m
Load 1 | Current | Ground | J3 | 18 | 1.1685m | 6.2596m
Load 1 | Current | Ground | J3 | 17 | 1.1572m | 6.2537m
Load 1 | Current | Ground | J3 | 20 | 1.1699m | 6.2604m
Load 1 | Current | Ground | J3 | 2 | 1.1281m | 6.2382m
Load 1 | Current | Ground | J3 | 3 | 1.1271m | 6.2377m
Load 1 | Current | Ground | J3 | 6 | 1.1379m | 6.2434m
Load 1 | Current | Ground | J3 | 5 | 1.1311m | 6.2398m
Load 1 | Current | Ground | J3 | 8 | 1.1438m | 6.2465m
Load 1 | Current | Ground | J3 | 9 | 1.1409m | 6.245m
Load 2 | Current | Power | J16 | 16 | -11.994 | 100m
Load 2 | Current | Ground | J16 | 13 | 1.1114m | 19.993m
Load 2 | Current | Ground | J16 | 1 | 1.1315m | 20.005m
Load 2 | Current | Ground | J16 | 4 | 1.1303m | 20.004m
Load 2 | Current | Ground | J16 | 7 | 1.1226m | 20m
Load 2 | Current | Ground | J16 | 10 | 1.1189m | 19.998m

Component Definition Summary:

ID | Ref Des | Type | In+ Pins | In- Pins | Out+ Pins | Out- Pins | S+ | S- | Vout (V) | Efficiency (%) | Ibias (A) | Resistance | Load Current (A) | Vmin | Vmax | Iout max (A) | PD max (W) | Pin Current max (A)
Source 1 | IC23 | Linear | IC23-2 | IC23-1 | IC23-5 | | | | -12 | | 0 | | | | | 200m | 1
Load 1 | J3 | Current | J3-26 | J3-2,3,5,6,8,9,11,12,14,15,17,18,20,21,23,24 | | | | | | | | | 100m | 11.4 | 12.6
Load 2 | J16 | Current | J16-16 | J16-1,4,7,10,13 | | | | | | | | | 100m | 11.4 | 12.6

## Figure <29>: Current density



## Figure <30>: Voltage



Network Simulation Messages Details

Type | Text
Info | Generated the settings file: C:\Users\piotr\Downloads\temp\PCB\PDNAnalyzer_Output\Fast_Servo\Power\Fast_Servo.py
Info | Simulation Progress: 10%
Info | Simulation Progress: 78.55%
Info | Simulation Progress: 100%
Info | Load and analyze result for Power
Info | No violations
Info | Analysis Complete Power

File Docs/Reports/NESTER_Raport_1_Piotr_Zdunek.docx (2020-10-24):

Projekt „Niskolatencyjny, synchroniczny i skalowalny system SDR” (NESTER)

Piotr Zdunek

Romera 10/39 02-784

Raport z pracy o dzieło z prawami autorskimi pt.:
„Opracowanie schematów i PCB modułu EEM z układem FPGA”
zrealizowanej w okresie od 13.01.2020 r. do 26.02.2020 r.
Pracę wykonał Piotr Zdunek

Celem pracy było opracowanie schematów i PCB modułu EEM z układem FPGA
Realizacja pracy obejmowała:

- Analizę wymagań
- Analiza opóźnienia systemu ADC-FPGA-DAC
- Dobór komponentów
- Realizację schematów

Wynikiem pracy jest:

- Zbiór wymagań pozwalających na realizację systemu

https://github.com/sinara-hw/Fast_Servo/wiki/Requirements

System requirements:

- FastServo shall resemble the Stabilizer architecture and mechanical design
- FastServo shall support PoE, Ethernet, USB interfaces (the same as Stabilizer)
- FastServo shall support Trenz FPGA modules - e.g. TE0710-02-35-2CF or TE0712-02-100-2C
- FastServo shall support 2x fast ADC channels
- FastServo shall support 2x fast DAC channels
- FastServo shall support 1 or 2 EEM connectors routed to the FPGA (to be discussed)

DAC subsystem requirements:

- DAC channel shall have latency + BW suitable for 3MHz closed-loop applications (including latency of loop filter on FPGA)
- DAC channel shall have fixed +-1V input/output range
- DAC channel bandwidth shall be 100 MHz or 125MHz 16bit

ADC channel requirements

- ADC channel AFE shall be based on FmcAdc100M14 design (https://ohwr.org/project/fmc-adc-100m14b4cha/wikis/home)
- ADC channel shall use LTC2195 as an ADC
- ADC channel bandwidth shall be 100 or 125MHz 16bit
- Analiza opóźnienia toru danych ADC-FPGA-DAC (prace jeszcze trwają)

https://docs.google.com/document/d/1A6bej79ME2-iZyJ6t_FZ-XkVyk64ExRZh2uJX7Lg3b4/edit?usp=sharing

- Dobór komponentów
  - ADC – LTC2195 – porównanie różnych układów https://docs.google.com/spreadsheets/d/1j0nTGpnnnBx4UXwtZlGYXvdnvVj7PuF5h2WQjEc7hA4/edit?usp=sharing

MFN Part number | No. CH | Sample rate [GSPS] | Bits | INL | DNL | Latency | Price [USD] | Project used
DAC3xJ82 | 2 | 1.6/2.5 | 16 | 6 | 4 | | 100
DAC5682Z | 2 | 1 | 16 | 4 | 2 | | 54
LTC2000 | 1 | 2.5 | 16 | 1 | 0,5 | 11 cycles (DAC clk - up to 2500 MHz), for 500 MHz, latency = 11*2 = 22 ns | 127 | Shuttler
~~AD9125~~ | ~~2~~ | ~~1~~ | ~~16~~ | ~~3,7~~ | ~~2,1~~ | ~~64 cycles (1 x interpolation~~ ~~fdac~~ ~~up to 1 GHz) + FIFO delay, depending on the mode(8 reg deep), for 500 MHz~~ ~~fdac~~~~, latency = 64*2 + 8*2 = 144 ns~~ | ~~50~~
MAX5898 | 2 | 0,5 | 16 | 3 | 1 | 2.9 ns (tpd) + 1.4 ns (td) + 22 cycles (500 MHz) = 2.9 + 1.4 + 44 = 48.3 ns (for 1 x interpolation) | 27
AD9783 | 2 | 0,5 | 16 | 4 | 2 | 7 cycles (7 ns * 2ns = 14 ns) + SET/HLD setup (to be analysed) approx. 2.4 ns = 16.4 ns | 43 | NIST servo
AD9747 | 2 | 0.25 | 16 | 4 | 2 | 7 cycles (250 MHz DAC CLK), latency = 7*4 = 28 ns
MAX5875/ | 2 | 0.2 | 16 | 3 | 2 | 1.1 ns + 9 cycles *5 ns = 46.1 ns
MAX5878 | 2 | 0.25 | 16 | 3 | 2 | 9 cycles (500 MHz clk) latency = 9*2 = 18 ns
AD9788 | 2 | 0.8 | 16 | 3.7 | 2.1 | 40 cycles (800 MHz clk) latency = 40*1.25 ns = 50 ns
AD9117 | 2 | 0.125 | 14 | 1.2 (precalibration), 0.6 (postcalibration) | 1.4 (precalibration), 0.6 (postcalibration) | 4 cycles for 1 channel, 3.5 cycles for second channel (input latched on falling edge), data clock = 125 MHz, latency = 4*8ns = 32 ns | 15

  - DAC – AD9117 – porównanie różnych układów

https://docs.google.com/spreadsheets/d/1_hZ97hf2xaO5iiprr2quBoDU6UxvHmOqcvnQKTeb41w/edit?usp=sharing

MFN Part number | Channels | Sample rate [MSPS] | Bits | INL | DNL | Latency | SFDR dBc (fin=10MHz) | Price [USD] | Project used
AD9461 | 1 | 130 | 16 | 5 | 0,6 | | 90 | 107
LTC2107 | 1 | 210 | 16 | 1,6 | 0,4 | | 103 (for fin=5 MHz) | 140 | CCD GK camera
LTC2195 | 2 | 125 | 16 | 2 | 0,5 | 1.1ns+2*tser + 4ns + 7*4 ns pipeline delay = 34 ns | 90 | 160 | NIST servo
ADS42LB69 | 2 | 250 | 16 | 3 | 0,6 | | Not sure. | 240
ADS5483 | 1 | 135 | 16 | 3 | 0,5 | | 98 | 135
LTC2209 | 1 | 160 | 16 | 5,5 | 1 | | 100 | 116

  - FPGA – moduł TE07020
- schemat elektryczny urządzenia zawierający dobrane komponenty (prace jeszcze trwają). Załączam dwa zrzuty schematów z projektu.
  - Układ DAC


- Moduł FPGA


Spis treści

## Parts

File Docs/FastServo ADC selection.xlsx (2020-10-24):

MFN Part number | Channels | Sample rate [MSPS] | Bits | INL | DNL | Latency | SFDR dBc (fin=10MHz) | Price [USD] | Project used | Comment | Link
AD9461 | 1 | 130 | 16 | 5 | 0.6 |  | 90 | 107
LTC2107 | 1 | 210 | 16 | 1.6 | 0.4 |  | 103 (for fin=5 MHz) | 140 | CCD GK camera |  | https://www.analog.com/media/en/technical-documentation/data-sheets/2107fb.pdf
LTC2195 | 2 | 125 | 16 | 2 | 0.5 | 1.1ns+2*tser + 4ns + 7*4 ns pipeline delay = 34 ns | 90 | 160 | NIST servo | tpd - typical propagation delay, t_ser - serial data rate,
ADS42LB69 | 2 | 250 | 16 | 3 | 0.6 |  | Not sure. | 240
ADS5483 | 1 | 135 | 16 | 3 | 0.5 |  | 98 | 135
LTC2209 | 1 | 160 | 16 | 5.5 | 1 |  | 100 | 116

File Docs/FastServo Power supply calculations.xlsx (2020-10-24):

Rail | Output voltage | Input voltage | Component | Current [mA] | Power [mW] | Efficiency [%] | Dissipated power [mW] | Total power [mW] | Current for input supply [mA]
P1V8 | 1.8 | 5.5 | TE07020 | 192 | 345.6 | 0.95 |  | 363.7894737 | 66.14354067
P3V3 | 3.3 | 5.5 | TE07020, AD7266, P1V8A, P2V5A | 1426 | 4705.8 | 0.95 |  | 4953.473684 | 900.6315789
P5V0A | 5 | 5.5 | ADA4817 | 58 | 290.00 | 0.9090909091 | 29 | 319 | 58
P2V5A | 2.5 | 3.3 | ADA4930 | 65 | 162.5 | 0.7575757576 | 52 | 214.5 | 65
P1V8A | 1.8 | 3.3 | LTC2195, SI5340 | 344 | 619.2 | 0.5454545455 | 516 | 1135.2 | 344
P3V3A | 3.3 | 5.5 | SI5340,AD9117, LTC6406, AD7266 | 216 | 712.80 | 0.6 | 475.2 | 1188 | 216
N5V0A | -5 | -5.5 | ADA4817 | 58 | 290 | 0.9090909091 | 29 | 319 | 58
N2V5 | -2.5 | -5.5 | ADA4930 | 65 | 162.5 | 0.4545454545 | 195 | 357.5 | 65
P5V5 | 5.5 | 12 | P1V8,P3V3,P5V0A | 1182.77512 | 6505.263158 | 0.9 |  | 7228.070175 | 602.3391813
N5V5 | -5.5 | 12 | N2V5A,N5V0A | 123 | 676.5 | 0.9 |  | 751.6666667 | 62.63888889
P12V | 12 | 12 | P5V5,N5V5 | 664.9780702 | 7979.736842 | 0.87 |  | 9172.111313 | 764.3426094
P12V0 | P5V5 | P3V6 | N6V0
 | P5V0A | P3V3A | N5V0
 | P3V3 | P2V5A | N2V5
 | P1V8 | P1V8A
Component | Rail [V] | Current consumption [mA]
ADA4817 | P5V0A | 58 |  |  | P
ADA4817 | N5V0A | 58
ADA4930 | P2V5A | 65
ADA4930 | N2V5A | 65
SI5340 | P3V3A | 115 | 173
SI5340 | P1V8A | 120
TE0720 | P3V3 | 1000
TE0720 | P1V8 | 150
LTC6406 | P3V3A | 18 |  |  | In | Out | Component
AD9117 | P3V3A | 55 |  |  | P12V0 | P5V5 | LTM4622
AD9117 | P3V3 | 13 |  |  |  | P3V6 | LTM4622
LTC2195 | P1V8A | 224 | 344 |  | P3V6 | P2V5A | LT1761/LT3042
LTC2195 | P1V8 | 42 |  |  | P5V5 | P3V3 | EN6347
AD7266 | P3V3 | 4 |  |  | P5V5 | P3V3A
AD7266 | P3V3A | 3
AD5722 | P6V0A
AD5722 | P3V3

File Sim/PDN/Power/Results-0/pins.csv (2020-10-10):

refdes | pin | voltage | current
T5 | 3 | 11.9973 | 0.550673
T5 | 2 | 11.9973 | 0.550673
T5 | 1 | 11.9973 | 0.550673
IC12 | 10 | -0.00107545 | -0.826009
IC12 | 7 | -0.00107545 | -0.826009
IC10 | 5 | 3.29773 | 0.1621427286
IC10 | 6 | 3.29773 | 0.1621427286
IC10 | 7 | 3.29773 | 0.1621427286
IC10 | 8 | 3.29773 | 0.1621427286
IC10 | 9 | 3.29773 | 0.1621427286
IC10 | 10 | 3.29773 | 0.1621427286
IC10 | 11 | 3.29773 | 0.1621427286
IC10 | 26 | -0.000648396 | -0.05989999999999998
IC10 | 13 | -0.000648396 | -0.05989999999999998
IC10 | 14 | -0.000648396 | -0.05989999999999998
IC10 | 15 | -0.000648396 | -0.05989999999999998
IC10 | 16 | -0.000648396 | -0.05989999999999998
IC10 | 17 | -0.000648396 | -0.05989999999999998
IC10 | 18 | -0.000648396 | -0.05989999999999998
IC10 | 32 | -0.000648396 | -0.05989999999999998
IC10 | 39 | -0.000648396 | -0.05989999999999998
U10 | 5 | 1.7987 | 0.16125
U10 | 6 | 1.7987 | 0.16125
U10 | 15 | 1.7987 | 0.16125
U10 | 7 | 1.7987 | 0.16125
U10 | 21 | -0.00065756 | -0.08205870000000001
U10 | 3 | -0.00065756 | -0.08205870000000001
U10 | 4 | -0.00065756 | -0.08205870000000001
U10 | 19 | -0.00065756 | -0.08205870000000001
U10 | 17 | -0.00065756 | -0.08205870000000001
R139 | 2 | 5.49734 | 1.66701
IC11 | 9 | -0.000992486 | -0.6597200000000001
U9 | H2 | -5.50022 | -0.0137889
U9 | H1 | -5.50022 | -0.0137889
U9 | G2 | -5.50022 | -0.0137889
U9 | G1 | -5.50022 | -0.0137889
U9 | F2 | -5.50022 | -0.0137889
U9 | F1 | -5.50022 | -0.0137889
U9 | E5 | -5.50022 | -0.0137889
U9 | E4 | -5.50022 | -0.0137889
U9 | E3 | -5.50022 | -0.0137889
U9 | E2 | -5.50022 | -0.0137889
U9 | E1 | -5.50022 | -0.0137889
U9 | D5 | -5.50022 | -0.0137889
U9 | D4 | -5.50022 | -0.0137889
U9 | D3 | -5.50022 | -0.0137889
U9 | D2 | -5.50022 | -0.0137889
U9 | D1 | -5.50022 | -0.0137889
U9 | C2 | -5.50022 | -0.0137889
U9 | C1 | -5.50022 | -0.0137889
U9 | H5 | -0.000465084 | 0.042455099999999996
U9 | H4 | -0.000465084 | 0.042455099999999996
U9 | H3 | -0.000465084 | 0.042455099999999996
U9 | G5 | -0.000465084 | 0.042455099999999996
U9 | G4 | -0.000465084 | 0.042455099999999996
U9 | G3 | -0.000465084 | 0.042455099999999996
U9 | F5 | -0.000465084 | 0.042455099999999996
U9 | F4 | -0.000465084 | 0.042455099999999996
U9 | F3 | -0.000465084 | 0.042455099999999996
IC22 | 7 | 12.9998 | 0.2001
IC22 | 5 | 0.0 | 0.0
IC22 | 4 | -12.9998 | -0.2001
IC3 | 10 | 2.4989 | -0.0324491
IC3 | 9 | 2.49893 | -0.0324747
IC3 | 4 | 2.499 | -0.03253
IC3 | 3 | 2.49902 | -0.032546
IC3 | 25 | 5.39272e-05 | 0.0
R106 | 2 | 2.49965 | -0.01
LD6 | 1 | 0.000127283 | 0.01
IC20 | 18 | 1.79962 | -0.014401
IC20 | 21 | 1.79964 | -0.0144092
IC20 | 26 | 1.79962 | -0.0143985
IC20 | 29 | 1.7996 | -0.0143881
IC20 | 32 | 1.79959 | -0.0143791
IC20 | 34 | 1.79958 | -0.0143751
IC20 | 39 | 1.79951 | -0.0143277
IC20 | 40 | 1.7995 | -0.0143216
IC20 | 45 | 0.000213913 | 0.235
IC2 | 15 | 1.79864 | -0.0574827
IC2 | 16 | 1.79865 | -0.0574843
IC2 | 51 | 1.79865 | -0.0574863
IC2 | 52 | 1.7988 | -0.0575465
IC2 | 53 | 0.00024733 | 0.0255682
IC2 | 2 | 0.000265123 | 0.0255608
IC2 | 5 | 0.000264487 | 0.0255611
IC2 | 13 | 0.000277602 | 0.0255557
IC2 | 22 | 0.00026698 | 0.0255601
IC2 | 33 | 0.000334819 | 0.0655319
IC2 | 45 | 0.000281022 | 0.0255542
IC2 | 47 | 0.000282841 | 0.0255535
IC2 | 49 | 0.000281283 | 0.0255541
JB1 | 16 | 3.29612 | -0.0714525
JB1 | 14 | 3.29611 | -0.0714498
JB1 | 12 | 3.2961 | -0.0714473
JB1 | 10 | 3.29609 | -0.0714418
JB1 | 6 | 3.29602 | -0.071407
JB1 | 4 | 3.29602 | -0.0714043
JB1 | 2 | 3.296 | -0.0713975
JB1 | F1 | -0.000108742 | 0.0277553
JB1 | F2 | -0.000393869 | 0.0278968
JB1 | 54 | -0.000185628 | 0.0277935
JB1 | 53 | -0.000128706 | 0.0277652
JB1 | 43 | -8.8912e-05 | 0.0277455
JB1 | 33 | -8.86843e-05 | 0.0277454
JB1 | 30 | -0.000131662 | 0.0277667
JB1 | 25 | -7.55034e-05 | 0.0277388
JB1 | 19 | -4.85411e-05 | 0.0277255
JB1 | 7 | -4.40913e-05 | 0.0277233
JB1 | 1 | -3.9258e-05 | 0.0277209
JB1 | 63 | -0.000131682 | 0.0277667
JB1 | 64 | -0.000176296 | 0.0277888
JB1 | 73 | -0.000182186 | 0.0277918
JB1 | 74 | -0.000239781 | 0.0278203
JB1 | 83 | -0.00018655 | 0.0277939
JB1 | 89 | -0.00023289 | 0.0278169
JB1 | 90 | -0.00028921 | 0.0278448
JB2 | 7 | 3.29594 | -0.124994
JB2 | 5 | 3.29594 | -0.124996
JB2 | 3 | 3.29594 | -0.124996
JB2 | 1 | 3.29596 | -0.125014
JB2 | F1 | 8.44812e-05 | 0.0668637
JB2 | F2 | -7.15954e-05 | 0.0671433
JB2 | 60 | 0.0002356 | 0.06659290000000001
JB2 | 59 | 0.000244906 | 0.0665763
JB2 | 50 | 0.000233902 | 0.066596
JB2 | 49 | 0.000259073 | 0.0665508
JB2 | 40 | 0.000230595 | 0.06660189999999999
JB2 | 39 | 0.000239204 | 0.06658649999999999
JB2 | 29 | 0.000244675 | 0.0665766
JB2 | 19 | 0.000243099 | 0.0665795
JB2 | 69 | 0.000226604 | 0.066609
JB2 | 70 | 0.00019348 | 0.06666839999999999
JB2 | 79 | 0.000210448 | 0.066638
JB2 | 80 | 0.000195134 | 0.0666655
JB2 | 89 | 0.000147578 | 0.0667506
IC4 | 5 | 3.29642 | -0.001
IC4 | 3 | 7.87403e-05 | 0.001
IC5 | 5 | 3.29642 | -0.001
IC5 | 3 | 6.75687e-05 | 0.001
IC15 | 4 | 3.29647 | -0.016
IC15 | 2 | -0.000273931 | 0.016
IC6 | 21 | 3.29649 | -0.00249967
IC6 | 17 | 3.29652 | -0.00250033
IC6 | 11 | -0.00029351 | 0.00333332
IC6 | 2 | -0.000292847 | 0.00333329
IC6 | 25 | -0.000294534 | 0.00333339
IC1 | 3 | 3.29642 | -0.000499999
IC1 | 2 | 3.29642 | -0.000500001
IC1 | 9 | 4.18968e-05 | 0.000499997
IC1 | 1 | 4.07355e-05 | 0.000500003
J4 | 34 | 3.29632 | -0.1
J4 | 10 | -7.13828e-05 | 0.0100144
J4 | 7 | -0.000105518 | 0.0100332
J4 | 4 | -0.000107901 | 0.0100345
J4 | 1 | -0.00013668 | 0.0100503
J4 | 19 | -2.19066e-05 | 0.00998718
J4 | 16 | -2.6781e-05 | 0.00998986
J4 | 13 | -6.30343e-05 | 0.0100098
J4 | 30 | 5.35905e-05 | 0.00994565
J4 | 25 | 1.39882e-05 | 0.00996743
J4 | 22 | 1.3207e-05 | 0.00996786
U6 | 32 | 3.29642 | -0.00299993
U6 | 31 | 3.29643 | -0.00300007
U6 | 33 | 8.64953e-05 | 0.00216694
U6 | 29 | 8.87247e-05 | 0.0021668
U6 | 19 | 9.00343e-05 | 0.0021667199999999996
U6 | 6 | 9.49737e-05 | 0.002166419
U6 | 5 | 9.39401e-05 | 0.002166479
U6 | 1 | 9.12604e-05 | 0.002166643
U7 | 14 | 3.29649 | -0.005
U7 | 25 | -6.25423e-05 | 0.000713863
U7 | 15 | -6.31448e-05 | 0.00071388
U7 | 18 | -9.55173e-05 | 0.000714805
U7 | 19 | -9.43502e-05 | 0.000714772
U7 | 20 | -9.35455e-05 | 0.000714749
U7 | 21 | -9.32625e-05 | 0.000714741
U7 | 1 | -3.89473e-05 | 0.000713189
IC2 | 34 | 1.79169 | -0.04
IC6 | 5 | 1.79824 | -0.005
JB2 | 6 | 1.79165 | -0.166688
JB2 | 4 | 1.79164 | -0.166671
JB2 | 2 | 1.79161 | -0.166641
J15 | 1 | 1.79838 | -0.0999999
JB3 | F2 | 4.91959e-05 | 0.00586566
JB3 | F1 | -4.75404e-05 | 0.00591687
JB3 | 5 | 6.59149e-06 | 0.00588821
JB3 | 6 | -8.52409e-06 | 0.00589622
JB3 | 11 | 5.06053e-06 | 0.00588902
JB3 | 12 | -1.2305e-05 | 0.00589822
JB3 | 17 | 2.60304e-05 | 0.00587792
JB3 | 18 | 7.39784e-06 | 0.00588779
JB3 | 23 | 1.93645e-05 | 0.00588145
JB3 | 24 | 3.6666e-06 | 0.00588976
JB3 | 29 | 3.53449e-05 | 0.00587299
JB3 | 30 | 2.02818e-05 | 0.00588097
JB3 | 35 | 3.83208e-05 | 0.00587142
JB3 | 36 | 1.65675e-05 | 0.00588293
JB3 | 45 | 4.92562e-05 | 0.00586563
JB3 | 46 | 3.9272e-05 | 0.00587091
JB3 | 55 | 5.24057e-05 | 0.00586396
U5A | 2 | 3.29983 | -0.00600018
U5A | 10 | 3.29983 | -0.00599992
U5A | 11 | 3.29983 | -0.00599992
U5A | 3 | 0.000156114 | 0.00449992
U5A | 9 | 0.000156037 | 0.00449992
U5A | 12 | 0.000157151 | 0.00449986
U5A | 17 | 0.000148449 | 0.00450032
U5B | 11 | 3.29985 | -0.00599995
U5B | 10 | 3.29985 | -0.0060002
U5B | 2 | 3.29985 | -0.00599986
U5B | 17 | 0.00014313 | 0.00450041
U5B | 12 | 0.000152685 | 0.00449991
U5B | 9 | 0.000156724 | 0.00449969
U5B | 3 | 0.00015077 | 0.00450001
U6 | 3 | 3.29982 | -0.007
IC20 | 8 | 3.29945 | -0.0599909
IC20 | 9 | 3.29947 | -0.0600093
U1 | 17 | 3.29971 | -0.0350075
U1 | 26 | 3.29968 | -0.0349926
U1 | 6 | 0.000119851 | 0.0700001
U4A | 6 | 4.99945 | -0.0589998
U4A | 17 | 0.000119042 | -1.0000000000287557e-07
U4B | 6 | 4.99941 | -0.0589998
U4B | 17 | 0.000110731 | -1.0000000000287557e-07
IC3 | 22 | -2.49919 | 0.0324985
IC3 | 21 | -2.49919 | 0.0324982
IC3 | 16 | -2.49918 | 0.0324947
IC3 | 15 | -2.4992 | 0.0325085
U4A | 12 | -4.99941 | 0.0295048
U4A | 4 | -4.99939 | 0.0294952
U4B | 12 | -4.99949 | 0.029517
U4B | 4 | -4.99941 | 0.0294829
J16 | 15 | 11.9944 | -0.0999998
J16 | 13 | 6.00077e-05 | 1.4000000000000123e-05
J16 | 1 | 8.03547e-05 | -1.0500000000000093e-05
J16 | 4 | 7.90884e-05 | -8.899999999999186e-06
J16 | 7 | 7.13369e-05 | 3.999999999976245e-07
J16 | 10 | 6.75647e-05 | 4.8999999999986554e-06
J3 | 25 | 11.9977 | -0.1
J3 | 21 | 0.000108175 | -8.659999999999744e-06
J3 | 23 | 0.000107992 | -8.460000000000065e-06
J3 | 24 | 0.000118802 | -1.996000000000029e-05
J3 | 11 | 9.61977e-05 | 4.060000000000175e-06
J3 | 12 | 0.000104321 | -4.559999999999807e-06
J3 | 14 | 0.000110255 | -1.0880000000000438e-05
J3 | 15 | 0.000103939 | -4.160000000000448e-06
J3 | 18 | 0.000118254 | -1.9380000000000265e-05
J3 | 17 | 0.00010711 | -7.539999999999457e-06
J3 | 20 | 0.000119762 | -2.0979999999999437e-05
J3 | 2 | 7.73227e-05 | 2.411999999999987e-05
J3 | 3 | 7.6515e-05 | 2.4979999999999968e-05
J3 | 6 | 8.72977e-05 | 1.3520000000000372e-05
J3 | 5 | 8.05563e-05 | 2.0679999999999484e-05
J3 | 8 | 9.32641e-05 | 7.17999999999986e-06
J3 | 9 | 9.05745e-05 | 1.0040000000000222e-05
J3 | 26 | -11.9977 | 0.1
J16 | 16 | -11.9955 | 0.0999998
IC9 | 8 | 9.00823e-05 | 5e-05
IC9 | 11 | 9.00239e-05 | 5e-05
IC16 | 11 | 8.69093e-05 | 5e-05
IC16 | 8 | 8.71022e-05 | 5e-05
IC18 | 6 | 5.49282 | -0.0777000333
IC18 | 2 | 5.49282 | -0.0777000333
IC18 | 1 | 5.49282 | -0.0777000333
IC18 | 11 | 9.25363e-05 | 3.33338e-05
IC18 | 8 | 9.26229e-05 | 3.33338e-05
IC18 | 5 | 9.68315e-05 | 3.33324e-05
IC19 | 1 | 5.49306 | -0.05905
IC19 | 2 | 5.49306 | -0.05905
IC19 | 8 | 9.47712e-05 | 5e-05
IC19 | 11 | 9.49519e-05 | 5e-05
IC17 | 2 | -5.4955 | 0.1181
IC17 | 1 | 8.48487e-05 | -0.0001
IC8 | 2 | -5.49559 | 0.1301
IC8 | 1 | 8.31008e-05 | -0.0001
IC21 | 2 | 12.9991 | -0.10005
IC21 | 1 | 12.9991 | -0.10005
IC21 | 11 | 5.58282e-05 | 3.33343e-05
IC21 | 8 | 5.57983e-05 | 3.33343e-05
IC21 | 5 | 6.17419e-05 | 3.33314e-05
IC23 | 2 | -12.9989 | 0.2001
IC23 | 1 | 3.66276e-06 | -0.0001
IC10 | 20 | 5.49589 | -0.271962
IC10 | 21 | 5.49588 | -0.271942
IC10 | 19 | 5.49589 | -0.271962
IC10 | 33 | 5.49244 | -0.265234
U10 | 1 | 5.49586 | -0.0783109
U10 | 2 | 5.4958 | -0.0782752
U10 | 18 | 5.49555 | -0.0781205
IC11 | pdna_pin_8_1 | 11.9918 | -0.251916
IC11 | pdna_pin_8_2 | 11.9918 | -0.251916
IC11 | pdna_pin_8_3 | 11.9918 | -0.251701
IC11 | pdna_pin_8_4 | 11.9918 | -0.251757
U9 | B5 | 11.9956 | -0.033473
U9 | B4 | 11.9956 | -0.0334737
U9 | A5 | 11.9956 | -0.0334743
U9 | A4 | 11.9956 | -0.0334751
IC22 | 1 | 11.9868 | -0.51083
IC22 | 3 | 0.000132342 | 0.51083
IC9 | 9 | 2.49993 | 0.07
IC9 | 10 | 2.49993 | 0.07
IC16 | 10 | 1.79993 | 0.1725
IC16 | 9 | 1.79993 | 0.1725
IC18 | 10 | 3.30022 | 0.1165
IC18 | 9 | 3.30022 | 0.1165
IC19 | 9 | 5.00022 | 0.059
IC19 | 10 | 5.00022 | 0.059
IC17 | 5 | -4.99991 | -0.118
IC8 | 5 | -2.49991 | -0.13
IC21 | 10 | 12.0 | 0.1
IC21 | 9 | 12.0 | 0.1
IC23 | 5 | -12.0 | -0.2
L12 | 1 | 11.9878 | -0.510829
L12 | 2 | 11.9878 | 0.510829
L10 | 1 | 12.9997 | -0.2001
L10 | 2 | 12.9997 | 0.2001
L11 | 1 | 12.9995 | -0.2001
L11 | 2 | 12.9995 | 0.2001
L13 | 1 | -12.9997 | 0.2001
L13 | 2 | -12.9997 | -0.2001
L14 | 1 | -12.9995 | 0.2001
L14 | 2 | -12.9995 | -0.2001

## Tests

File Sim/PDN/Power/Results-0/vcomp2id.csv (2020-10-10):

vrefdes | id
VCOMP0 | 0
VCOMP1 | 1
VCOMP2 | 2
VCOMP3 | 3
VCOMP4 | 4
VCOMP5 | 5
VCOMP6 | 6
VCOMP7 | 7
VCOMP8 | 8
VCOMP9 | 9
VCOMP10 | 10
VCOMP11 | 11
VCOMP12 | 12
VCOMP13 | 13
VCOMP14 | 14
VCOMP15 | 15
VCOMP16 | 16
VCOMP17 | 17
VCOMP18 | 18
VCOMP19 | 19
VCOMP20 | 20
VCOMP21 | 21
VCOMP22 | 22
VCOMP23 | 23
VCOMP24 | 24
VCOMP25 | 25
VCOMP26 | 26
VCOMP27 | 27
VCOMP28 | 28
VCOMP29 | 29
VCOMP30 | 30
VCOMP31 | 31
VCOMP32 | 32
VCOMP33 | 33
VCOMP34 | 34
VCOMP35 | 35
VCOMP36 | 36
VCOMP37 | 37
VCOMP38 | 38
VCOMP39 | 39
VCOMP40 | 40
VCOMP41 | 41
VCOMP42 | 42
VCOMP43 | 43
VCOMP44 | 44
VCOMP45 | 45
VCOMP46 | 46
VCOMP47 | 47
VCOMP48 | 48
VCOMP49 | 49
VCOMP50 | 50
VCOMP51 | 51
VCOMP52 | 52
VCOMP53 | 53
VCOMP54 | 54
VCOMP55 | 55
VCOMP56 | 56
VCOMP57 | 57
VCOMP58 | 58
VCOMP59 | 59
VCOMP60 | 60
VCOMP61 | 61
VCOMP62 | 62
VCOMP63 | 63
VCOMP64 | 64
VCOMP65 | 65

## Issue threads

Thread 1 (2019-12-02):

sinara-hw/Fast_Servo #1: [RFC] New EEM: Fast Kasli Servo

dtcallcock, 2019-12-02:
A fresh issue for one of the two boards proposed in [[RFC] Sinara Servo sinara-hw/meta#16](https://github.com/sinara-hw/meta/issues/16).

This would be a high performance board using the FPGA on a Kasli to run the feedback loop.  Board would have ADCs, DACs and all the required analog electronics.

- Roughly equivalent capabilities to the [NIST servo] (https://arxiv.org/abs/1508.06319) (100MSPS parallel DACs/ADCs, few 100ns latency).
- Able to do direct digital modulation/demodulation for things like PDH locks.
- Would need quite a few EEMs. 
- Need to consider timing issues if using ribbon cables.  Could be made as a daughterboard that stacks onto Kasli and uses the EEMs as board to board connectors to avoid this but that would limit us to 1 per Kasli.
- High cost, approaching $1k/ch

gkasprow, 2019-12-02:
There is also [ open source](https://github.com/antmicro/zynq-video-board) design that uses Enclustra SO-DIMM modules.

jordens, 2019-12-02:
Yes. My point was just that FMC seems to be designed to offer you front panel real estate, i.e. is more suited to "front ends" while an FPGA module can live somewhere in the back and doesn't need what FMC gives.

gkasprow, 2019-12-02:
I meant FMC carrier card, not FMC module with FPGA:)

gkasprow, 2019-12-02:
Below is Stabilizer with Enclustra module. It fits nicely
[image]

gkasprow, 2019-12-02:
I'm just looking at pinout tables and there are compatible boards with Artix (MarsAX3), Spartan(Mars MX2), Zynq 7(Mars ZX3), Zynq US (Mars XU3) and Cyclone V SoC(Mars MA3). The only potential issue is only 22 LVDS pairs available. Trenz has at least twice more. In the case of dual parallel ADC and DAC, this may be not enough.

hartytp, 2019-12-02:
> The fact that we are trying to do both DC accuracy and stability and very wide bandwidth is a bit worrying to me though.

Indeed. I largely feel this board should be for closed-loop or AC-coupled applications, so DC accuracy/stability should not be necessary.

The only motivation for DC I've come across for this design is the general "it would be great to have a general-purpose board with some fast ADCs/DACs and an FPGA for sinara"...

dhslichter, 2019-12-02:
> "it would be great to have a general-purpose board with some fast ADCs/DACs and an FPGA for sinara"...

Sounds like the original motivation for Sayma 1.0 :stuck_out_tongue_closed_eyes: Beware the feature creep...

gkasprow, 2019-12-02:
Well, we will also have DC-coupled slow ADC and DAC. So in principle, with some effort, one can combine slow DC processing chain  and fast AC processing chain to get wideband operation.

hartytp, 2019-12-02:
Something like a 2 channel pdq with a decent speed ADC would be a really useful addition to Sinara

gkasprow, 2019-12-02:
Any idea what ADCs and DAC would you want for such application?
I have to spend some money in next two weeks so can buy some eval kits or Trenz modules :)

hartytp, 2019-12-02:
Others may feel differently but I’d go for the same dac as pdq / shuttler. And a decent 16 bit (dc precise) 20Hz parallel ADC. Caveat is that I haven’t given this design much thought and don’t have a clear use case in mind for it right now...

gkasprow, 2019-12-02:
I've just ordered        [ TE0710-02-35-2CF](https://shop.trenz-electronic.de/en/TE0710-02-35-2CF-Dual-fast-Ethernet-Artix-Module-with-Xilinx-Artix-7-35T-Speedgrade-2C) and  [TE0712-02-100-2C](https://shop.trenz-electronic.de/en/TE0712-02-100-2C-FPGA-Module-with-Xilinx-Artix-7-XC7A100T-2FGG484C-1-GByte-DDR3-4-x-5-cm) directly from Trenz.
These are nice modules available online from both Trenz and Digikey. Digi is slightly more expensive if you ship them back to EU :)
I already have devkit for DAC used in Shuttler.
This [ADC ](https://pl.mouser.com/datasheet/2/609/AD9461-878087.pdf)looks interesting. Parallel interface and 5bit INL
MUch more expensive but with [1.5bit INL](https://www.analog.com/media/en/technical-documentation/data-sheets/2107fb.pdf). And it uses DDR/CMOS interface.

dhslichter, 2019-12-03:
> Others may feel differently but I’d go for the same dac as pdq / shuttler.

FWIW the tentative Shuttler design plan is to use a <1 LSB DNL/INL 14-bit DAC with dithering to achieve additional bits at DC, with a fallback of using two DAC channels as coarse/fine.  The PDQ DACs are not recommended for new designs, will be EOL soon.  It's challenging to find a high-speed 16-bit DAC with good DC properties and reasonable power/cost.

dhslichter, 2019-12-03:
> And a decent 16 bit (dc precise) 100MSPs parallel ADC

This will be an expensive ADC....

gkasprow, 2019-12-08:
We can copy entire AFE from [this project](https://ohwr.org/project/fmc-adc-100m14b4cha/wikis/home) and only replace ADC with i.e. [LTC 2107](https://www.analog.com/media/en/technical-documentation/data-sheets/2107fb.pdf)
Are there any applications that require DC-coupling of DAC?

gkasprow, 2020-01-03:
My colleague @zdun8 will take care of this project.
Let's close specifications so he could continue.

hartytp, 2020-01-03:
Yeah, it would be interesting to hear what use-cases people might have for this card...

For the use-cases I have in mind, something like an [ AD9262BCPZ-10](https://www.analog.com/media/en/technical-documentation/data-sheets/AD9262.pdf) would be interesting for the input. Not too expensive (~£40/channel in singles); 10MHz analog input BW (640MHz sample rate); 16 bits; decently DC precise; 15dB noise figure; 300mW/channel.

That's fast enough for all the applications I have in mind

hartytp, 2020-01-03:
My chief aim would be something that's "like stabilizer but faster" e.g. for DC-precise feedback loops with a few MHz closed-loop BW. Combining one of those ADCs with a decent >=~75MHz DAC (ideally 16-bit, but 14-bit might also work, DNL of a few etc) would do the job nicely.

hartytp, 2020-01-04:
hmmm...that ADC won't work as the latency is way too high -- almost 1k cycles of the 640MH modulator clock unless I'm misreading the data sheet. Probably no ADC like that will work for this because of latency. :(

hartytp, 2020-01-04:
Anyway, at a high-level, what I'd like to see is:
- 2 channel card that's mechanically compatible with Stabilizer
- latency + BW suitable for 3MHz closed-loop applications (including latency of loop filter on FPGA)
- fixed +-1V input/output range (+-10V range and PGIAs are nice, but not so easy at this BW)
- PoE for stand alone applications
- 1 or 2 EEM connectors routed to the FPGA. Example use case for this is running this card as an EEM driven by Kasli using the FPGA as a SERDES (using the 1.5GBPs/EEM link developed for Fastino/Phaser)
- maybe add an extra high-speed AFE mezzanine connector if there is space and we can find something that works with the current stackup height.

I'd focus on the feedback/fast servo application for this rather than worrying about anything else. Having the option to use it as a fast ADC/DAC EEM adds another nice extra use-case for free.

---

Designing a SDR card is fun, but orthogonal to the fast servo and would probably want a different design (AC-coupled RF front end rather than DC-precise) so best left to a separate project when/if someone has a use-case/specification for it.

I don't personally see any benefit from trying to make this fast enough to do all digital PDH locks now that we have pounder. And, in any case, an all digital PDH card would presumably want a different design (e.g. 3 DACs per ADC, one for the modulation RF output, one for the "fast/laser current lock" output and one for the "slow/PZT lock" output).

gkasprow, 2020-01-04:
This is a sigma-delta modulator so it has several drawbacks. The resolution depends strongly on the effective sampling rate. That's why the bandwidth is just a few MHz.
Another is the latency - it needs a lot of filtering and decimation to get 16bits of resolution.
I used in the past LTC2107 for CCD imaging and I'm not sure we would find better ADC.
Recently I used 4 x fast [ 5MS/s 18bit](https://www.analog.com/media/en/technical-documentation/data-sheets/AD7960.pdf) converts to increase the sampling rate, but it is not straight-forward.
Faster [10MS/s 18bit SAR](https://pl.mouser.com/datasheet/2/609/238618f-1271669.pdf) converters are also available.

hartytp, 2020-01-04:
The [phase metrology] use-case is interesting. It'd be nice to have a 2 channel ADC for this purpose (rather than two single-channel ADCs).

hartytp, 2020-01-04:
@gkasprow I'll leave component choice to you. :)

hartytp, 2020-01-04:
@gkasprow I'll leave component choice to you. :)

Although, do check out the prior art like the [NIST servo](https://arxiv.org/pdf/1508.06319.pdf), the red pitaya etc

hartytp, 2020-01-04:
(e.g. the [ADC](https://www.analog.com/media/en/technical-documentation/data-sheets/219543f.pdf) on the NIST servo seems quite nice)

zdun8, 2020-01-05:
Hello All, 
It's nice to meet you all and I'm happy to help with the project. Let's summarize the specification of the board. 

- ADC we go for LTC2107 with AFE from [FMC-ADC 100M14b4cha](https://ohwr.org/project/fmc-adc-100m14b4cha/wikis/home), yes?

- DAC - not decided yet? As far as I understand we could use the one used in Shuttler project LTC2000?

hartytp, 2020-01-05:
Hi @zdun8 good to meet you!

Assuming we all agree (and since no one has said anything to the contrary yet, I'll assume we do) that the primary goal for this project is to build a digital feedback controller targeting a few MHz close-loop BW, then I think we can close this issue. Let's open separate individual issues for the ADC/DAC choice etc.

Before we settle on the ADC/DAC choice, can you:
- read the whole of this issue as there is some discussion about what features are important (e.g. overall latency)
- read the NIST servo paper linked above and understand what components they chose and why, as well as the performance they achieved
- also look into the red pitaya stuff (@jordens don't know if you have anything to add on this?)
- then compare/contrast the components you've chosen to the other systems so we know why you've chosen them (e.g. may even be worth producing a table with latency, noise, temp co, cost, power consumption, etc, for the various choices)

It's also worth giving some thought to the input/output front ends at this stage. What sample rate and what analog BW will you target? What latency do you expect for the FPGA stuff (LF etc)?

closed 2020-01-05 by hartytp

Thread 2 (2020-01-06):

sinara-hw/Fast_Servo #2: DAC IC selection

zdun8, 2020-01-06:
The goal of this issue is to discuss the selection of the DAC IC. 

The requirements for DAC channel are as follows:
-DAC channel shall have latency + BW suitable for 3MHz closed-loop applications (including latency of loop filter on FPGA)
-DAC channel shall have fixed +-1V input/output range
-DAC channel bandwidth shall be 100 MHz or 125MHz 
-DAC channel shall have 14 bit ENOB

One option is to use LTC2000, which is used in Shuttler project, but it's quite expensive. 
I have listed a similar ones in this spreadsheet: https://docs.google.com/spreadsheets/d/1j0nTGpnnnBx4UXwtZlGYXvdnvVj7PuF5h2WQjEc7hA4/edit?usp=sharing

Feel free to update the spreadsheet.

gkasprow, 2020-01-07:
In case of DACs, please also look at the tempco

hartytp, 2020-01-07:
And again latency will be key...

gkasprow, 2020-01-24:
@hartytp is it critical for your applications to have dual-channel, well-matched DAC?

hartytp, 2020-01-24:
> @hartytp is it critical for your applications to have dual-channel, well-matched DAC?

It's always nice to have matching, but that's an extremely weak preference that can/should be overridden by other factors (e.g. cost/performance/simplicity).

The main case where I'd want matched DACs would be IQ mixers etc, but for that I think we should make a separate SDR design with AC-coupled RF AFE. In any case, Phaser solves all our RF DAC needs for now.

gkasprow, 2020-01-24:
And what about tempco? [These](https://datasheets.maximintegrated.com/en/ds/MAX5898.pdfl) Maxim DACs are low cost and offer 1LSB DNL but would be their  110ppm gain tempo be real killer?

hartytp, 2020-01-25:
> would be their 110ppm gain tempo be real killer?

The primary application for this design is closed-loop, so temp co is irrelevant.

A low temp co can be nice for other secondary uses (e.g. a generic DAC+ADC+FPGA design), but I wouldn't want to compromise the design's main goals over that, so if there are no comparable DACs with low temp co then it's not an issue.

gkasprow, 2020-01-25:
The decision is to either use high-end and expensive LTC2000 or one of low-cost DACs

hartytp, 2020-01-25:
@gkasprow My gut feeling is that we should go for the low-cost DAC.

Before making the final call, @zdun8 could you post a table that compares, the LTC2000, MAX chip, AD9783 (NIST servo) and anything else you think is interesting. Include all the interesting things like cost, power consumption, temp co, INL/DNL, noise, etc, etc. I assume this will be good material for your thesis anyway.

zdun8, 2020-01-25:
I have updated the spreadsheet with the information about some DACs that I've found. 
@gkasprow do you have MAX5898 in mind? In general it seems, that it could do the job if we turn off the interpolation, then the delay is small, and SFDR is very good. One limitation is that the input data is interleaved (for Q and I outputs), but with 500 MSPS I think we are fine. 

I think LTC2000 is very expensive and has only one channel. Comparing AD9783 and MAX5898 they present similar performance. MAX has lower INL and DNL, but it has higher latency approx. 48 ns comparing to 16 ns of the AD for 500 MHz DAC clock. MAX is cheaper 27 USD vs 43 USD. Please check if my analysis is correct, I could only find that AD9783 latency is 7 cycles in the datasheet. 

https://docs.google.com/spreadsheets/d/1j0nTGpnnnBx4UXwtZlGYXvdnvVj7PuF5h2WQjEc7hA4/edit?usp=sharing

gkasprow, 2020-01-25:
We do not need 500MS/s but max 125MS/s.  AD9783 has +/2bit DNL which makes it actually 14bit DAC

hartytp, 2020-01-26:
What's our latency budget?

gkasprow, 2020-01-26:
I was targeting 100ns,
We are anyway limited by analog BW and setting time.

hartytp, 2020-01-26:
> I was targeting 100ns,

For the DAC, or for the whole thing?

> I have updated the spreadsheet with the information about some DACs that I've found.

I think you can write off the AD9125 due to unacceptable latency.

> AD9783 has +/2bit DNL which makes it actually 14bit DAC

That's probably okay for this application. More resolutionis nice but non-critical.

gkasprow, 2020-01-26:
I meant 100ns or so, for entire chain

zdun8, 2020-01-27:
Then we don't have a lot of timing budget. From the DACs that I've analysed AD9783 has the smallest latency (7 cycles). It's been also used in NIST servo. Another option would be MAX5878.

hartytp, 2020-01-27:
> I meant 100ns or so, for entire chain

That doesn't leave a lot for the DAC...I guess we can clock the DAC at a higher rate (but only changing the value every few samples). This feels sufficiently tight that we need a full system model before finalizing this choice. But, I suspect we can rule out anything that's more than, say 10 cycles of latency. At that point the list starts to look rather short...

gkasprow, 2020-01-27:
It does not have to be just 100ns, 150 or even 200ns would be probably fine. THe FPGA also needs a few clock cycles to do even simple algorithm.

hartytp, 2020-01-27:
Sure, I agree we can spare an extre 1-2 clock cycles in the DAC, but a latency of, say, 20 cycles is probably not going to cut it (unless we run the DACs at a very high clock speed). So worth reducing our options to only cover cases with an acceptable latency.

As this is also a critical parameter, I think we'll need a full system model sooner rather than later.

hartytp, 2020-01-28:
> I guess we can clock the DAC at a higher rate (but only changing the value every few samples).

Actually, I suppose that doesn't help. To reach higher sample rates, I suspect we'd need a SERDES in the FPGA which would add additional latency. So, without doing a full simulation including FPGA code that meets timing, I'm not sure we can assume a DAC clock rate above 125MHz...

dhslichter, 2020-02-04:
One option to consider is the AD9117, which we are testing out as a Shuttler candidate DAC.  It runs at 125 MSPS with 4 cycles of latency (32 ns), two channels, 14 bits, <0.5 LSB DNL/INL, relatively low power, low cost.

zdun8, 2020-02-09:
@gkasprow Would 14 bit DAC be sufficient for Fast Servo? Initial requirement was to use at least 16 bit DAC.

zdun8, 2020-02-12:
After discussion with @gkasprow we decided that AD9117 is a valid option for Fast Servo. 
It has 4 cycles of delay at 125 MSPS and provides an autocalibration mechanism that lowers the INL and DNL to +/- 0.6 LSB. @hartytp what do you think about this DAC?

hartytp, 2020-02-13:
That looks ok. What's the preference for this v AD9783? I don't feel strongly, just curious....

gkasprow, 2020-02-13:
It has longer latency, with low cost FPGA one won't be able to drive it with 500MHz anyway, DNL of +/- 2 LSB makes it essentially 14bit DAC, +/-4LSB makes it 13-bit precise

hartytp, 2020-02-13:
Fair enough. I haven't checked the specs in detail but assuming the DC performance, noise, stability, etc of the AD9117  look good then go for it!

dhslichter, 2020-02-13:
FWIW we are currently testing AD9117 to verify datasheet performance and look for any other "gotcha"s.  On the list include DC stability, noise, ability to dither to achieve higher effective bits at DC, measuring tempco, etc.  This will all get put into the Shuttler repository once tests are done.  So far, haven't run across anything that would preclude its use here, especially since the fact that it's part of a closed loop will address slow drifts and tempco.  Definitely monotonic at 14 bits, including major carries, but you have to run the autocalibration routine to get this performance (very simple, no external components required).

zdun8, 2020-02-23:
@gkasprow is programmable gain needed for DAC AFE also?

gkasprow, 2020-02-23:
I don't think so

zdun8, 2020-02-23:
Ok

closed 2021-06-16 by gkasprow

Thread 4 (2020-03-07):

sinara-hw/Fast_Servo #4: Analog Inputs AFE design

zdun8, 2020-03-07:
Hello, 

As suggested I'm creating a separate thread for the dicussion about the AFE design for Analog Channels. Current requirements of the AFE are as follows:
AFE shall have:
- adjustable gain 
- high CMRR for low frequencies
- low latency / phase lag
- should allow for 3 MHz loop bandwidth 

AD8251 which was used in NIST servo might be too slow for our design, whereas the CERN design will have low CMRR compared to an instrumential amplifier.

hartytp, 2020-03-07:
NB A really good reference for the basics is https://www.analog.com/media/en/training-seminars/design-handbooks/designers-guide-instrument-amps-complete.pdf

It's not trivial to build a high-impedance differential front end with >>3MHz BW, good CMRR (AC + DC) and switchable gain. Will need thought and simulation (and thinking about all the nasties like Ron temp co etc that can easily trash the stability of the amp)

gkasprow, 2020-03-07:
Why do we need to make it high-impedance?

hartytp, 2020-03-07:
I guess you're right...anything high-impedance will probably be low BW so stabilizer can be used. Still, nice to have a setting which gives 10k or so.

zdun8, 2020-03-07:
What gain values exactly do we require? Is gain 1 a requirement? There is a high bandwidth instrumentation amplifier MAX4445, but it is not unity gain stable, minimum gain is 2, higher gains can be achieved by changing a value of resistor which we could do with opto switches.

hartytp, 2020-03-08:
Let's not talk about gains, but rather input ranges.

IMHO for a faster board like this, a +-1V input range is the only one that's critical.

We could consider a +-10V range, but that might be challenging due to slew rates. If it turns out to be impractical, I'd be okay with dropping or replacing with, say, a +-5V range.

A +-0.1V range (or +-0.25V or whatever is easy to implement) could also be nice.

hartytp, 2020-03-08:
I haven't looked at that MAX chip in detail, but we'd need to look at offsets, noise, temp co, etc in detail to make sure it's up to the job. Otherwise, we can build our own from high-speed OpAmps, with will need to think carefully about CMMR, noise, stability, etc (taking into account all relevant parasitics). That's not so hard, but will take a bit of work. Good learning experience for a masters' project though...

zdun8, 2020-03-08:
Hmm I already have masters degree, I don't need another one :D  I'm helping with the project in my spare time, I think it's really interesting. 

Okay, I will look into the simulation, but it seems to me that it's usually easier to use an IC than to use separate components.

hartytp, 2020-03-08:
> Hmm I already have masters degree, I don't need another one :D 

Sorry! It's hard with these online projects to track who is doing what.

> I'm helping with the project in my spare time, I think it's really interesting.

Cool! 

> Okay, I will look into the simulation, but it seems to me that it's usually easier to use an IC than to use separate components.

Completely agree. It's always better to use an IC than to roll ones own (IC designers can make use of matching tricks that are hard with discrete components). I'm just not aware of any good fast PGIAs available off the shelf.

The other option is to accept that PGIA is hard and just have a unity gain diff amp. It would reduce the flexibility a bit but wouldn't be the end of the world.

zdun8, 2020-03-10:
> IMHO for a faster board like this, a +-1V input range is the only one that's critical.
>
> We could consider a +-10V range, but that might be challenging due to slew rates. If it turns out to be [...]

What is the common mode voltage of the input signal? 0V ?

hartytp, 2020-03-11:
Yea approx 0V just some small amounts of ground nosie

gkasprow, 2020-03-11:
What if we take the standard fully diff amp and add two opto-MOS switched resistors in the FB loop?
Something like [this](http://www.ti.com/lit/ds/symlink/ths770006.pdf) which has  CMRR
[image]

What CMRR are we aiming for? Let's say for 10MHz

jordens, 2020-03-11:
Common mode will typically be differential mode divided by two. Not 0 V.

hartytp, 2020-03-11:
> Common mode will typically be differential mode divided by two. Not 0 V.

hartytp, 2020-03-11:
> What if we take the standard fully diff amp and add two opto-MOS switched resistors in the FB loop?
> Something like this which has CMRR

That could potentially work. We'd need to pay attention about all the usual things like Ron (variations/temp co/matching), capacitance matching, bandwidth, noise, etc.

Out of curiosity, what are the pros/cons of that configuration compared with a "classic" InAmp.

> What CMRR are we aiming for? Let's say for 10MHz

I'm not too worried about the HF CMRR since the CMC + RFI filter should give very good rejection of that. It's more the DC and lower frequencies that we need to watch for.

zdun8, 2020-03-15:
> What if we take the standard fully diff amp and add two opto-MOS switched resistors in the FB loop?
> Something like [this](http://www.ti.com/lit/ds/symlink/ths770006.pdf) which has CMRR

This is a fixed gain fully diff amp, maybe THS4509 or PGA870 would be a better option?

I fear that we might have a significantly lower CMRR due to imperfect feedback resistor matching  with opto-MOS switchable resistors, this can be tricky. What do you think?

gkasprow, 2020-03-15:
True, the opto-MOS have non-calibrated ON resistances. We can use one fully differential amp with 1x gain that gives good CMRR and then another one with programmable gain using opto-MOS which would work as an ADC driver. The PGA870 has 30mV offset which is a lot for 14-bit system

hartytp, 2020-03-15:
Yeah a diff amp and a pgia might be the way to go so long as the diff amp doesn’t add to much noise.

zdun8, 2020-03-29:
Could you have a look at this Tina simulation? I have used THS77006 as an input stage and THS4509 as a PGA witch selectable gain through switches (currently ideal). Strangely, the transient simulation shows some distortion on the output VM3, do you know why this might be?

Few points: the AFE currently supports +/- 100 mV input (switches on), and +/-1 V input (switches on). The signal source needs to be adjusted accordingly. 
https://www.dropbox.com/s/p5dsm860ver8yfn/fast_servo_ths77006_ths4509_tran_v1t.TSC?dl=0

[image]
[image]

hartytp, 2020-03-29:
> Could you have a look at this Tina simulation

Who are you asking?

zdun8, 2020-03-30:
> > Could you have a look at this Tina simulation
> 
> Who are you asking?

Anyone, perhaps you @hartytp  or @gkasprow might have an idea what's going on?  Any help would be highly appreciated.

zdun8, 2020-03-30:
Okay, problem is solved. @gkasprow  suggested that I should run the simulation for a longer period 50 ns, as at the begining there will be a transient state, which will cause distortions. Thanks!

hartytp, 2020-03-30:
Nice! Good catch @gkasprow

zdun8, 2020-04-23:
Finally, I have come up with a draft for the AFE using the initial approach with the instrumentation amplifier. 

TL;DR; Two input voltage ranges were simulated 100 mV and 1 V. CMRR is 56 dB for 0-3 MHz for 1V input signal and 50 dB for 100 mV.
RFI filter is set for 10 MHz for differential signal. 

Attaching schematics and simulation report. I'll be happy to hear any suggestions!
[image]

CMRR plot (signal amplitude 1 V ): 
[image]

Transient plot (signal amplitude 100 mV, frequency 1 MHz):
[image]

AC plot (signal amplitude 1 V):
[image]

More details can be found in the report:
https://docs.google.com/document/d/1smgiGiFC6XPziigHHxrSAG0CFXy-PrKfYR3dXpd6QYk/edit?usp=sharing

Sim file for transient: 
https://www.dropbox.com/s/j2d94vl1exfmxap/fast_servo_tran_v2.asc?dl=0

Sim file for AC
https://www.dropbox.com/s/6mvxo21uil9o3ib/fast_servo_ac_v2.asc?dl=0

Sim file for CMRR 
https://www.dropbox.com/s/0210zgl2mrteqy2/fast_servo_cmrr_v5.asc?dl=0

hartytp, 2020-04-23:
Do you have a noise sim?

For the CMRR and other simulations, are you assuming all components have their nominal values, or did you do a monte-carlo/whatever to look at variance?

zdun8, 2020-04-23:
Adding noise figure measured on the output:
[image]

I have just set the components to 0.1% tolerance for resistors, but I think the standard sim doesn't take that into account. I will prepare a Monte Carlo or a worst case scenario simulation. This is not so straightforward, because I think we should used a matched resistor pairs for the feedback resistors.

dtcallcock, 2020-04-23:
Do you have a sense of likely robustness without TVS or similar?  

As I mentioned, the front-ends die all the time on the NIST boxes.

zdun8, 2020-04-24:
There is no information in the datasheet about any input protection. Also an evaluation board for the ADA4817 opamp doesn't have any.

Maybe we can add a high value limiting resistor and low leakage TVS on the input?

Attaching CMRR simulations with Monte Carlo component variance and worst case scenario. Unfortunately it seems that part value variance degrades the CMRR higher frequencies.  RFI filter capacitors 5% tolerance is causing that. We can increase the input filter bandwidth to accommodate for that. 

1. Monte Carlo part value variance. Resistors' tolerance 0.1%, capacitors' 5%. 100 runs. 
[image]

2. Monte Carlo part value variance. Resistors' tolerance 0.1%, capacitors' 5%. 5 runs. Temperature change sweep 0 -> 80 degrees with 20 degree step. 
[image]

3. Worst case simulation. 100 runs. 
[image]

4. Monte Carlo part value variance. Resistors' tolerance 0.1%, capacitors value fixed 5 runs. 
[image]

gkasprow, 2020-04-24:
We need protection diodes as in Stabilizer. They can affect the CMRR due to non-linear capacitance

zdun8, 2020-04-26:
I have modified the RFI filter a bit. I think we don't need low pass filter on each input, common mode choke does the job of filtering common noise, and mismatch of these capacitors significantly impacts the CMRR.

New AFE:
[image]

Modified filter also results in better CMRR and AC characteristics. Plots with protection diodes for 1V input signal, parts value is modeled with Monte Carlo function, 10 runs. Resistors' tolerance 0.1%, capacitors 5%. 

CMRR:
[image]

Noise:
[image]

AC:
[image]

 If the SPICE model from here https://www.diodes.com/part/view/BAV199 is correct the diodes don't affect the CMRR significantly.

gkasprow, 2020-04-26:
The CMRR can be affected by differences between the diodes. That's why it's better to use quad pack diodes which have similar capacitances. The diode capacitance depends strongly on voltage but we assume the CM voltage is the same.

hartytp, 2020-04-26:
@zdun8 can you put the noise plots on a log log axis please? I can't read the noise floor from the plots (just the flicker noise).

hartytp, 2020-04-26:
How does the Ron temp co/matching affect the gain stability + CMMR? Have you estimated the overall gain stability (I'd just do a back of the envelope on paper, looking at the most sensitive parts). What about the switch temp co? NB you have quite low resistor values, which will accentuate the FET imperfections.

What's the self-heating with a FS input and +-11.5V (or whaterver) supplies? You have quite low resistor values so I can imagine this getting hot.

hartytp, 2020-04-26:
Aah, sorry, forgot we're only supporting +-1V max, so the power consumption is less of an issue.

hartytp, 2020-04-26:
A 4pF differential capacitor is quite small, what do you think the parasitics will be?

hartytp, 2020-04-26:
Is that enough capacitance to drive the ADC? Do you also need a differential capacitor for the ADC?

hartytp, 2020-04-26:
What's the motivation for removing the shunt capacitors to ground on the inputs? Won't they help to improve the AC CMMR?

hartytp, 2020-04-26:
What range of offsets do you expect due to resistor tolerances. IME it's usually worth using resistor networks for the gain/subtraction resistors to avoid annoying input offsets that need to be calibrated out later on.

hartytp, 2020-04-26:
Anyway, nice work!

zdun8, 2020-04-27:
> can you put the noise plots on a log log axis please? I can't read the noise floor from the plots (just the flicker noise).

Noise plot for 1 V input signal:
[image]

Noise plot for 100 mV input signal:
[image]

> How does the Ron temp co/matching affect the gain stability + CMMR? Have you estimated the overall gain stability (I'd just do a back of the envelope on paper, looking at the most sensitive parts). What about the switch temp co?

Not yet. What do you think would be the best way to simulate this?

> A 4pF differential capacitor is quite small, what do you think the parasitics will be?

Not sure. We can increase the value of the capacitor if we decrease the value of series resistors. 

> Is that enough capacitance to drive the ADC? Do you also need a differential capacitor for the ADC?

Which capacitor you mean exactly? Of the filter on the output of the LTC6406? 
[image]

> What's the motivation for removing the shunt capacitors to ground on the inputs? Won't they help to improve the AC CMMR?

According to this app note https://www.analog.com/media/en/training-seminars/tutorials/MT-070.pdf page 4, the common mode choke does the same job so the capacitors can be removed. Also when simulating with Monte Carlo part value variance, the CMRR was heavily affected by the mismatch of those values, but it's also possible that my simulation is wrong. The app note suggests that C9 should be 10xC7, but that's difficult to achieve if we want to have the cut off frequency for common mode at 10 MHz and similar for differential.  Attaching some plots:

Schematic of the RFI filter:
[image]

CMRR with the RFI filter capacitors at fixed values, rest of the compontents with Monte Carlo part value variability. 
[image]

CMRR with all components with Monte Carlo part variability. 
[image]

> What range of offsets do you expect due to resistor tolerances. IME it's usually worth using resistor networks for the gain/subtraction resistors to avoid annoying input offsets that need to be calibrated out later on.

Totally agreed. Not sure about the offsets, we need to be careful about the resistors. 

> Anyway, nice work!

Thanks :)

hartytp, 2020-05-05:
Thanks @zdun8!

> Noise plot for 100 mV input signal:

Nit pick: I assume that's RTO, not RTI. I generally prefer RTI plots but in either case please do specify so we know what to look at. 

It's hard to read the noise plots without a grid (another nit pick, please always add a grid and ideally a marker!). AFAICT, the RTI noise for the +-1V setting is approx 10nV/rtHz. Which is pretty good (e.g. same as the AD8253 on Sampler/Stabilizer). I'm assuming it's also about 10nV/rtHz for the 100mV setting, in which case we're doing pretty well.

> Not yet. What do you think would be the best way to simulate this?

@gkasprow what do you think about simulating the effects of Ron/leakage (tolerance plus temp co) on gain/offset accuracy and CMMR?
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

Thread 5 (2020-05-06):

sinara-hw/Fast_Servo #5: Analog outputs AFE design

zdun8, 2020-05-06:
Hello, 

I'm creating a new issue for AFE design for DAC channel. Could you please verify that these requirements are valid?

1. DAC channel shall have latency + BW suitable for 3MHz closed-loop applications (including latency of loop filter on FPGA)
2. DAC channel shall have fixed +-1V input/output range
3. DAC channel bandwidth shall be 100 MHz or 125MHz 14bit
4. DAC channel shall use AD9117 DAC
5. DAC channel load will be 50 Ohms

I would like to use ADA4930 FDA on the output to drive +/-1 V signal. What do you think? 
Thanks for your feedback!

hartytp, 2020-05-07:
> Analog output channel bandwidth shall be 100 MHz or 125MHz 14bit

The bandwidth is already covered by requirement (1) so no need to specify that. 

Other than that, that's about what I had in mind, but I'd feel much more comfortable if other users would chip in. (It's hard to be sure that anyone will actually use this if they don't make themselves heard...)

gkasprow, 2020-11-23:
There is an issue with DAC outputs.
In Stabilizer, the SMA connector case was kept on the GND level.
In Fast Servo it is driven in differential way so we loose compatibility. Coaxial cables are not designed to be driven symetrically - for that purpose twinax cables are used.
Please use only positive output of the amplifier

zdun8, 2020-11-24:
Thanks for the check, I'll fix it.

zdun8, 2020-11-25:
Shall we just terminate the N signal after the common mode inductor with 50 Ohms and connect the negative pins of SMA to GND?

[image]

I think simulations should be rerun for such change. Also, what's the point of using a differential output amplifier if we only need single ended output...

gkasprow, 2020-12-16:
yes, but mak the termination resistor DNP

closed 2021-06-16 by gkasprow

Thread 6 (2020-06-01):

sinara-hw/Fast_Servo #6: [RFC] Fast Servo HDL/Software features and specification

jmatyas, 2020-06-01:
Hi All, 

I was asked to develop software/HDL support for the Fast Servo (I'm going to use _FS_ as a shortcut), which I happily agreed upon. 

I've tried to gather specs and use-cases that have been already discussed to start designing implementaion worfkflow but what I found was mostly hardware specification or that FS should be "like stabilizer but faster", wich is rather vague desctiption.  I created this issue, to clarify Fast Servo's specs/features that are needed to be implemented. 

### Features
Fundamental questions: what FS should do, should be capable of (in terms of software/HDL)? What should be implemented? What are the needs? What is top priority?

And apart from the above:
  * what is it's desired mode of operation - standalone board capable of communicating with Kasli or FS as Kasli's "slave" board? (or both?)
  * if communicating with Kasli - what kind of communication is needed - logs, alerts, etc? Will basic configuration of the loops be enough?
  * running 2 independent voltage loops only? or maybe 1 input 2 outputs as well?
  * what kind of feedback control loop is needed - PID, PI, PD, PIID, etc?
  * what other features are needed?
  * what kind of control is needed (only "set coefficients, turn on, off", or something more?)
  * what kind of software/HDL support for Stabilizer mezannines is needed?

hartytp, 2020-06-01:
> I've tried to gather specs and use-cases that have been already discussed to start designing implementaion worfkflow but what I found was mostly hardware specification or that FS should be "like stabilizer but faster", wich is rather vague desctiption

Indeed! I'd really love to gather use cases here before we start developing gateware/firmware. So far this project has had way too little input from other users. I'd really like to hear more "end-user" voices.

The main use-case I had in mind for FS was laser frequency servos with ~1-3MHz BW. This would be  a standalone card controlled via Ethernet. 

> running 2 independent voltage loops only? or maybe 1 input 2 outputs as well?

I think that 2 independent loops is sufficient, but ideally with a mux to allow flexible mapping between ADCs and IIRs (assuming we have room in the timing budget).

> what kind of feedback control loop is needed - PID, PI, PD, PIID, etc?

PIID would be nice.

> what other features are needed?

Streaming ADC/IIR output samples for diagnostics is really useful.

dtcallcock, 2020-06-01:
There are a couple of use cases detailed in the [paper on the NIST design](https://tsapps.nist.gov/publication/get_pdf.cfm?pub_id=919237).

The doubling cavity use case is probably already well covered by Stabilizer though as only ~10kHz of bandwidth is needed.

In practice, the NIST box is also used a lot for laser intensity servo-ing.   SU-Servo, Phaser, and Sayma have this capability built-in though so that use case is probably already covered in Sinara too.

> So far this project has had way too little input from other users.

That's kind of an issue for Sinara in general.  You'd think with all those crates out there we'd be getting a bit more feedback.

jmatyas, 2020-06-03:
> The main use-case I had in mind for FS was laser frequency servos with ~1-3MHz BW. This would be a standalone card controlled via Ethernet

OK, so ARTIQ control (SU-Servo style) or something else? (This question may be derived from another one: do we want to integrate FS with ARTIQ software?)

> Streaming ADC/IIR output samples for diagnostics is really useful.

Oh, definitely! Seems like a nice feature.

And regarding features -  do we want FS to work with some kind of external phase-frequency detector, or auto-locking/phase detection system should be available in gateware as well?

hartytp, 2020-06-03:
> OK, so ARTIQ control (SU-Servo style) or something else? (This question may be derived from another one: do we want to integrate FS with ARTIQ software?)

For the "standalone" use-case I imagine this being non-real time, so just any convenient ethernet interface (c.f. stabilizer). Once it has a python driver it's ARTIQ-compatible.

> And regarding features - do we want FS to work with some kind of external phase-frequency detector, or auto-locking/phase detection system should be available in gateware as well?

There are a bunch of nice additional features once could imagine, including auto-relock/LD (@jordens has made some proposals for Stabilizer and elsewhere).

For laser locks, there would usually be an external mixer. e.g. on Pounder.

gkasprow, 2021-11-06:
@jordens does it make any sense to synchronize ADC and DAC using a low jitter clock from Kasli? I can add an MMCX clock input

jordens, 2021-11-07:
Yes. For all non-DC precision applications this is very useful.

gkasprow, 2021-11-07:
OK, I added MMCX input to the clock distribution IC input.

kaolpr, 2022-05-11:
Together with @jmatyas we're looking for some synergy for sw development for this project. I see two main directions:
- Port [linien](https://github.com/linien-org/linien). This should be pretty straightforward, however up to my understanding (please correct me if I'm wrong) it is less generic than our original "reference" - NIST Digital Servo.
- Use PYNQ as system base and port NIST Digital Servo architecture creating sort of a tool set that can be (more) easily adjusted to the particular application. As an example application we'd implement original NIST Servo so that one could use it as (almost) drop-in replacement.

Do you have any thoughts on that? Which option do you prefer?

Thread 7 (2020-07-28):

sinara-hw/Fast_Servo #7: Schematics draft - review request

zdun8, 2020-07-28:
Hello All, 

I would like to ask you to review the schematics of Fast Servo. They are in a draft stage, but from the electrical point of view they are almost complete. 

Thanks in advance!

zdun8, 2020-07-31:
There is one known issue. The analog clocks for ADC and DAC need to be externally generated by a dedicated IC.

dtcallcock, 2020-07-31:
Would it be possible to post a pdf?

zdun8, 2020-08-02:
Sure, but please give me some time. Due to the fact that I need to add a clock IC, the power supply has to be modified.

zdun8, 2020-08-06:
I have updated the schematics. Attaching a PDF file. As always the schematics are subject to change during the layout :) [
[Fast_Servo_Sch_Draft_V1.PDF](https://github.com/sinara-hw/Fast_Servo/files/5038604/Fast_Servo_Sch_Draft_V1.PDF)
](url)

closed 2021-06-16 by gkasprow

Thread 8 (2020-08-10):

sinara-hw/Fast_Servo #8: Component placement review

zdun8, 2020-08-10:
Hello, 

I have started working on the layout. Please have a look at the screenshots below showing the component placement. 
[image]

[image]

dtcallcock, 2020-08-11:
Is matching the Stabilizer header placement to allow compatibility with Stabilizer mezzanines possible/desirable?

zdun8, 2020-08-11:
I can check if it's possible. Could you send me the step files for the mezzanines? Or the links to the PCB projects?

dtcallcock, 2020-08-11:
Pounder is an example of such a mezzanine.  Hopefully everything you need is there in the [Pounder repository](https://github.com/sinara-hw/Pounder).

gkasprow, 2020-08-11:
@zdun8 we keep full mechanical and electrical (logic levels)  compatibility with Stabilizer. It will propagate to mezzanine compatibility as well. The only difference is missing 10V range.

zdun8, 2020-08-11:
To be honest, I have completely missed that requirement. I'll update the schematics and PCB accordingly.

zdun8, 2020-09-10:
Please check the updated placement. 
[image]
[image]

zdun8, 2020-09-16:
@gkasprow Yes, local power are only LDOs. 

Basic placement version of the PCB is on the repo.

closed 2021-06-16 by gkasprow

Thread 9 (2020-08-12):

sinara-hw/Fast_Servo #9: design review

gkasprow, 2020-08-12:
- [ ] arrange that all designators and texts do no overlap,  make sure they are not inverted (I know about Altium option)
- [ ] please add 0R option resistor that grounds input connectors
- [ ] add 0R between U1A and IC12 for debugging
- [ ] don't we need ESD protection for SD?
- [ ] did U do the power budget? How much power would LDOs dissipate? Please add a suitable note. use ADI tool for power tree simulation.
- [ ] was power sequencing implemented? One must make sure that no SOM signals are present before SOM is supplied
- [ ] please mark which banks are 3.3 and 1.8V rated
- [ ] why we need both R23 and R6?
- [ ] rename P1V0 -> REF1V0
- [ ] add 0R to J8 - L2, L4, just in case

zdun8, 2020-08-13:
Thanks for the review. I will introduce the changes and will let you know if I have any doubts.

zdun8, 2020-08-31:
> * don't we need ESD protection for SD?
There is a voltage level translator between the SD-Card and SoM, so additional ESD protection is not needed.

> * specify which Trenz modules can be used. Take into account the signalling standard and modules based on Artix, Kintex7 and Zynq

For now, we can support TE0712 (Artix), TE0715-15 (Zynq Artix), TE0715-30 (Zynq Kitex), TE7020 (Zynq Artix), is that okay? @gkasprow 

> * did U do the power budget? How much power would LDOs dissipate? Please add a suitable note. use ADI tool for power tree simulation
[image]

gkasprow, 2020-09-01:
are you sure the level converter has ESD protection?
Support for these modules is fine, just place an info on schematics

zdun8, 2020-09-01:
> are you sure the level converter has ESD protection?

Yes, is that enough? 
[image]

gkasprow, 2020-09-01:
ok, should be fine.

zdun8, 2020-10-25:
Routed PCB is ready for review on the repo. Please let me know if you find anything! 
 
I have checked the pinout in vivado for template projects for TE0720, TE0715-15 and TE0715-30 and the bitstream is properly generated. Archived projects are also available on the repo.

closed 2021-06-16 by gkasprow

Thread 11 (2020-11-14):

sinara-hw/Fast_Servo #11: CLK_100M assignment issue

jmatyas, 2020-11-14:
On TE0712 with Artix, CLK_100M is assigned to a pin (C19) that can only be used as the N side of a differential clock input. 

According to Xilinx 7 Series Clocking User Guide [UG472](https://www.xilinx.com/support/documentation/user_guides/ug472_7Series_Clocking.pdf) p. 31:
[image]

Vivado throws an error during compilation and won't allow past this issue, unless one accepts "non-optimal use of the N side of the clock capable pins" ([here](https://www.xilinx.com/support/answers/67599.html)).

zdun8, 2020-11-14:
Interesting, I didn't know that thanks. 

TE0712 is not supported on FastServo, only TE0720, TE0715-15 and TE0715-30. 

On TE0720 and TE0715 CLK_100M is connected to P capable pin, so it should work.

jmatyas, 2020-11-17:
> TE0712 is not supported on FastServo, only TE0720, TE0715-15 and TE0715-30.

Which module with Artix on board will be supported, then?  I emailed Greg a few days ago and he mentioned that a Trenz module with Artix shall be supported on Fast Servo (that's what the wiki page says, as well).

 Or is it not yet decided which module will be used?

zdun8, 2020-11-17:
Unfortunately I had to remove TE0712 support as it has one bank fixed at 3.3V and then it's impossible to be compatible with TE0720 and TE0715-15/30. 

TE0720 and TE0715 have Zynq with Artix FPGA and they are supported on FastServo. Is that okay for you? 

I will update the wiki with the compatible board list.

jmatyas, 2020-11-18:
It seems to be a sensible solution but I'm not sure about leaving the Artix module out. 

@gkasprow  what do you think about not supporting modules with "clean" Artix at all?

zdun8, 2020-11-18:
I totally understand your concern. Initially I thought that supporting different Trenz module will be straightforward, but unfortunately the devil is in the details and it's not easy to support all kinds of modules. 

I would suggest to leave it as it is right now, so TE0720, TE0715-15/30 are supported. I think it gives plenty of flexibility.

gkasprow, 2020-11-23:
So, for the moment we have only ZynQ devices supported? There is no full ARTIQ support for ZynQ right now.

gkasprow, 2020-11-23:
What is exactly the problem with 3V3 bank support? We need 3V3 bank anyway to keep compatibility with 3V3 levels of existing mezzanines

zdun8, 2020-11-23:
In short: on Artix module TE0712 on JM2 connector some pins have fixed voltage whereas on other  modules they are configurable (set via external pins). 

Please have a look on this spreadsheet: 

https://docs.google.com/spreadsheets/d/1bnEOR_nFoHTlCReCy4KJ_HS_cJoHPDwn3MEk9fibMuM/edit?usp=drivesdk

In order to be able to support Zynq Artix nad Zynq Kintex modules some IOs have to be fixed to some banks to allow 3.3V or 1.8V voltage standard support and signals on JM2 pins for TE0712 are fixed on 3.3V whereas on other modules we can change them to 1.8V from outside. We have limited amount of 3.3V and 1.8V signals and in order to support TE0712 we would have to add voltage translator buffers for 3.3V to 1.8V translation which in my opinion is an overkill. 

In the evening I will post schematics  of the modules that show the problem in a clearer way. 

Anyway, supporting different modules from Trenz is cumbersome.

zdun8, 2020-11-24:
The issue can be summarized to the following statement: there are not enough 1.8 V IOs on TE0712 to support it. 

I have compared TE0712, TE0720 and TE0715-15/30 in this spreadsheet https://docs.google.com/spreadsheets/d/1bnEOR_nFoHTlCReCy4KJ_HS_cJoHPDwn3MEk9fibMuM/edit?usp=sharing

Bank 14 which is connected to JB2 is 3.3 V fixed. If it was connected to JB2 pins as in other modules everything would work perfectly. Unfortunately there are not enough 1.8 V to move them to other bank/connector. 

[image]

[image]

gkasprow, 2020-12-16:
OK, let's leave only Zynq support then.

closed 2021-06-16 by gkasprow

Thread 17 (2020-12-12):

sinara-hw/Fast_Servo #17: [sch review] C22 connections

filipswit, 2020-12-12:
In current configuration pins 3, 4, 6, 8 and 1, 3, 5, 7 are tied together. I think you should rename net labels for 5, 6, 7, 8.

[image]
[image]

filipswit, 2020-12-13:
According to #12, it is in recommended design, but It still shows unconnected nets. My proposition is to add under dash suffix to eliminate it.

[image]

zdun8, 2020-12-20:
Electrically it's still the same net as they are shorted internally in the ADC, so it would be a confusing. I will add a note. 
I've added a rule to not generate DRC for this signals not being connected, but I don't know if there is a way not to show the unconnected nets in the PCB. 

I will change the schematics as follows so it will not generate DRC and will still be clear. 
[image]

closed 2021-06-16 by gkasprow

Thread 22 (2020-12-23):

### ISSUE TITLE
[sch review] IC10 connect PG 

### ISSUE THREAD

**Issue by filipswit** [sinara-hw/Fast_Servo#22]
Connect PG via 560R to PVIN
![image](https://user-images.githubusercontent.com/24258965/101988452-fa2f5180-3c99-11eb-8796-155f7b62a217.png)

**Comment by zdun8** [comment]
This resistor is optional and PG is not used for this DC/DC converter. 
![image](https://user-images.githubusercontent.com/5497039/102936538-a21df980-44a8-11eb-90ed-67b79f932bee.png)

**Comment by filipswit** [comment]
You are right, I based on table.

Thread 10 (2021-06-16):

### ISSUE TITLE
Missing resistor

### ISSUE THREAD

**Issue by jmatyas** [sinara-hw/Fast_Servo#10]
![image](https://user-images.githubusercontent.com/48015058/95773549-f776a700-0cbe-11eb-8c08-d92350626d04.png)

According to LTC2195 datasheet (p.23) SDO line should be equipped with an external 2k pull-up resistor in serial programming mode. 
Was leaving it out intentional or perhaps am I missing it somewhere?

**Comment by zdun8** [comment]
It's a mistake. I will fix it. Thank you!

What's interesting NIST servo didn't have the resistor on their board with the ADC, probably it's placed on the motherboard.

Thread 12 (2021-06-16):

### ISSUE TITLE
PCB issues

### ISSUE THREAD

**Issue by gkasprow** [sinara-hw/Fast_Servo#12]
@zdun8 please look at this
![obraz](https://user-images.githubusercontent.com/4325054/99980416-8095f900-2da8-11eb-8572-1f1e24455f4e.png)

**Comment by zdun8** [comment]
These pins are shorted internally in the ADC. 
![image](https://user-images.githubusercontent.com/5497039/100005731-b697a500-2dc9-11eb-95db-8580cdeb8a63.png)


https://www.analog.com/media/en/technical-documentation/data-sheets/219543f.pdf

**Comment by gkasprow** [comment]
so make them in such way that do not generate DRC errors.

**Comment by zdun8** [comment]
It is not generating DRC.

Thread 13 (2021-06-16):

### ISSUE TITLE
JTAG connector

### ISSUE THREAD

**Issue by gkasprow** [sinara-hw/Fast_Servo#13]
It's worth considering RA JTAG connector. Access to this one could be difficult due to mezzanine
![obraz](https://user-images.githubusercontent.com/4325054/99980617-b804a580-2da8-11eb-857e-efe640165327.png)
We can leave it for next release

**Comment by zdun8** [comment]
Good point. 

There was a keepout region in Stabilizer on the top and bottom border of the PCB so I have assumed the boards will be placed in some kind of rails, which would make access to right angle connector impossible.

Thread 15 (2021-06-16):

### ISSUE TITLE
[sch review] wrong supply voltage IC1

### ISSUE THREAD

**Issue by filipswit** [sinara-hw/Fast_Servo#15]
Input voltage should be 5V insted of 3.3V

**Comment by zdun8** [comment]
You are right. We don't have 5.0V supply on the board apart from the analog one. I suggest to use 5.5 V supply and a diode to comply with USB requirements. 
![image](https://user-images.githubusercontent.com/5497039/102711693-e304eb00-42bb-11eb-9513-4d4c124bb360.png)

**Comment by filipswit** [comment]
Looks fine.

**Comment by gkasprow** [comment]
BAS416 is 200mA diode. Replaced it with 1A one

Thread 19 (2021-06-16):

### ISSUE TITLE
[sch review] U9 wrong configuration of RT and FB

### ISSUE THREAD

**Issue by filipswit** [sinara-hw/Fast_Servo#19]
I don't understand why there is positive converter used to make negative voltage. But in these situation we should treat N5V5 as ground, so FB and RT should be referenced to N5V5 instead of GND.

**Comment by zdun8** [comment]
There is no problem with using this DC/DC converter to generate a negative voltage. It's very small and provides high output current. 

You are right regarding FB and RT, I will correct it, thank you.

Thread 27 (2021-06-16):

### ISSUE TITLE
[pcb review] U9 move input capacitor

### ISSUE THREAD

**Issue by filipswit** [sinara-hw/Fast_Servo#27]
DS: `Place the CIN capacitor as close as possible to the VIN
and GND connection of the LTM8029.`

![image](https://user-images.githubusercontent.com/24258965/102019119-cfb0c780-3d71-11eb-8e61-0e78f2972ae1.png)

**Comment by gkasprow** [comment]
right, the Cin should be connected to N5V5, not GND to close the AC loop

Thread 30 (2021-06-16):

### ISSUE TITLE
[pcb review] Input capacitors placement

### ISSUE THREAD

**Issue by filipswit** [sinara-hw/Fast_Servo#30]
DS: `The input capacitor needs to be placed as close as possible to the IC pins`
Looks like here is place for these caps.
![image](https://user-images.githubusercontent.com/24258965/102019817-e0633c80-3d75-11eb-8b84-f1520757abb0.png)

**Comment by zdun8** [comment]
Moved 100nF input capacitor closer to the input pins, thanks.

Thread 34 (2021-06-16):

### ISSUE TITLE
[pcb review] unmask vias from both sides on thermal pads

### ISSUE THREAD

**Issue by filipswit** [sinara-hw/Fast_Servo#34]

**Comment by zdun8** [comment]
For what reason?

**Comment by filipswit** [comment]
There is a danger of mask pocket.

**Comment by zdun8** [comment]
Brandner or other manufacturers has never complained to me regarding this, but we can change it to avoid this problem.

**Comment by gkasprow** [comment]
Actually, Brandner often complains about it:)

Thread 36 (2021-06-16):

### ISSUE TITLE
[pcb review] iregular pad shape

### ISSUE THREAD

**Issue by filipswit** [sinara-hw/Fast_Servo#36]
Why one of pads is different?

![image](https://user-images.githubusercontent.com/24258965/102022004-36d77780-3d84-11eb-96b1-700617fd4f56.png)

**Comment by zdun8** [comment]
To be honest I don't know, I copied the placement of the PoE Module from Stabilizer. Maybe @gkasprow  knows why it was done like this in that project.

**Comment by gkasprow** [comment]
It's such to increase the clearance between primary and secondary side

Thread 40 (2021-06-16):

### ISSUE TITLE
[pcb review] Overlay modifications

### ISSUE THREAD

**Issue by filipswit** [sinara-hw/Fast_Servo#40]
- [ ] Please use one direction of texts.

![image](https://user-images.githubusercontent.com/24258965/102022368-b403ec00-3d86-11eb-8d39-f0a74a9be50b.png)
![image](https://user-images.githubusercontent.com/24258965/102022444-25dc3580-3d87-11eb-908d-61d70c64943d.png)

- [ ] Move text

![image](https://user-images.githubusercontent.com/24258965/102022376-c2520800-3d86-11eb-8044-a76f04d3bc9b.png)
![image](https://user-images.githubusercontent.com/24258965/102022409-f4636a00-3d86-11eb-9c37-250201aba436.png)

- [ ] Rotate

![image](https://user-images.githubusercontent.com/24258965/102022427-09d89400-3d87-11eb-8f39-dd832cd971a0.png)

- [ ] Add connectors description on top overlay

**Comment by zdun8** [comment]
Fixed.

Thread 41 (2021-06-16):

### ISSUE TITLE
[pcb review] L4 polygon changes

### ISSUE THREAD

**Issue by filipswit** [sinara-hw/Fast_Servo#41]
- [ ] You can move tracks to connect this two polygons

![image](https://user-images.githubusercontent.com/24258965/102022943-54a7db00-3d8a-11eb-8369-b918d9af5fde.png)

- [ ] Remove these antennas

![image](https://user-images.githubusercontent.com/24258965/102022960-76a15d80-3d8a-11eb-8bc8-fb631fa5771c.png)

**Comment by zdun8** [comment]
Fixed. BTW grounded nets will not behave as antennas.

**Comment by gkasprow** [comment]
Actually, they can :)
They became resonators.

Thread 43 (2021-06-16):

### ISSUE TITLE
[pcb review] Modify ground connection

### ISSUE THREAD

**Issue by filipswit** [sinara-hw/Fast_Servo#43]
C125 is connected to GND with just one 0.254mm path, left side is unconnected, maybe add via on the left.
![image](https://user-images.githubusercontent.com/24258965/102135570-78d1ed80-3e58-11eb-96a0-a2f5b628712c.png)

**Comment by zdun8** [comment]
Fixed it in this way. 
![image](https://user-images.githubusercontent.com/5497039/103460382-0a28d700-4d16-11eb-9ff3-5a9f315b0705.png)

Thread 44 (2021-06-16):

### ISSUE TITLE
[pcb review] Modify connection

### ISSUE THREAD

**Issue by filipswit** [sinara-hw/Fast_Servo#44]
- [ ] Remove the track or modify plygon.

![image](https://user-images.githubusercontent.com/24258965/102135789-c3536a00-3e58-11eb-9fc6-0e9993bf2b3b.png)

- [ ]  Sides vias may not be connected to poly
![image](https://user-images.githubusercontent.com/24258965/102135991-175e4e80-3e59-11eb-91f5-477d99214d7e.png)

**Comment by zdun8** [comment]
Fixed, thanks

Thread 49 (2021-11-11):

### ISSUE TITLE
component availability

### ISSUE THREAD

**Issue by gkasprow** [sinara-hw/Fast_Servo#49]
some components are EOL or hard to find and need replacement
SMBJ5V0A -> SMBJ5.0A
EN6347QA -> MPM3840GQV-Z
AG5300 -> AG5412
ACPL-217-500E -> TCMD1000
DSC1001DL5-100.0000 - ~~DSC6101JE1A-000.0000~~ TC-100.000MBD-T
SI5340B-D-GM -> SI5340B or SI5340C
LTC6406IUD#PBF –> LTC6406IMS8E#PBF
SN74LVC1G125DCKT -> 74LVC1G14GW + 74LVC1G125W5-7 to preserve Stabilizer compatibility
EN5311QI ->  ~~FAN5354MPX~~ FAN8060EMPX
LTM8029IY#PBF ->MAX17577ATC+ 
R0603_32R2_0.1%_0.063W_10PPM ->~~30R 0.1% + 2.2R 0.1%~~ 31R6
TPS62175DQC -> FAN8060EMPX

**Comment by filipswit** [comment]
- [ ] EN6347QA -> MPM3840GQV-Z
RAMP capacitor should be between 10pF and 47pF

- [ ] SI5340B-D-GM -> SI5340B or SI5340C
Nothing has changed in description.

- [ ] IC24 FAN8060EMPX
inverted voltage divider

- [ ] TPS56637RPA looks to be hard to get

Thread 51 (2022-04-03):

sinara-hw/Fast_Servo #51: v1.0 debugging

gkasprow, 2022-04-03:
P3V3 is 3.2V instead of 3V3
PoE works
All rails work
Module with ZynQ board consumes 470mA without Silabs chip which still didn't arrive

gkasprow, 2022-04-03:
JTAG works, but XADC monitor shows 0

gkasprow, 2022-04-03:
XADC works after loading pre-built image from Trenz

jmatyas, 2022-08-05:
- Front Panel LEDs work
- Ethernet LEDs work
- LED1, LED2, LED3 works
- Si5340 configuration and programming via I2C successful ( #54 );  Si5340_nRST OK
- Clock_100M from OSC1 works
- UART works

### ADC LTC2195
- [x] SPI communication
- [ ] Data path
- [x] DCO path

### DAC AD9117
- [ ] SPI communication
- [x] Data Path (signal generation on both channels)

jmatyas, 2022-09-21:
Ethernet connection established

jmatyas, 2022-09-27:
ADC AUX AD7266
- [x] SPI communication OK
- [x] input address lines OK
- [x] range and SGL/!DIFF OK
- [x] sampled values OK

DAC AUX AD5722
- [x] SPI communication OK (both read and write)
- [x] BIN line OK
- [x] nCLR line OK
- [x] output values OK

jmatyas, 2022-10-27:
- microSD card slot and booting OK
- EEM I2C from EEM connector 
  - both LM75 OK
  - EEPROM OK
- GPIO header OK
- LVDS header OK

closed 2024-06-14 by kaolpr

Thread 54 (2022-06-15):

sinara-hw/Fast_Servo #54: Si5340 debugging

jmatyas, 2022-06-15:
- unable to communicate with Si5340 on I2C bus
- if nRST not driven, it floats up to 2.15 V
- every possible address from 0 to 255 has been tried out - no success
- after the master starts the transmission and sends the device address, a NACK is detected - always

Since, according to its part number, the Si5340 installed on Fast Servo is already pre-programmed, it is suspected that its voltage thresholds are incompatible with the 1.8 V from the SoM. It is currently being investigated:

- [ ]  remove SoM from carrier
- [ ] temporarily short 1.8 V from SoM with 3.3V so the SMPS generates all of the power supplies
- [ ] temporarily desolder pull-up resistors from the Si I2C lines
- [ ] pull-up lines to 3.3 V
- [ ] try to communicate with Si with the use of external I2C master controller
    - [ ] if successful, change NVM register value, so Si I2C voltage thresholds and communication switches to the one compliant with 1.8 V. **BE CAREFUL!!! The Si5340's NVM is programmable,  but only _ONCE_**

jmatyas, 2022-06-24:
Suspicion regarding I2V voltage thresholds confirmed. Switching I2C Bus voltage to 3.3V allowed to communicate with Si5340. Contents of the register under address 0x0943 confirm this.

Suggestion regarding next release: 

- since there may be problems from time to time with such matter, an idea that is worth considering is to place I2C bus voltage shifter between SoM and Si5340 from 1.8V to 3.3V (it would need further investigation and datasheet reading, however, a quick test revealed that after setting Si5340 I2C voltage thresholds to 1.8 V, communication on bus powered from 3.3V was still possible)

kaolpr, 2022-06-25:
Nice catch! Good that things start to look reasonable ;-)

Have you tried reprogramming Si5340 to use 1.8V?

I believe under normal circumstances this should not be a problem, as 1.8V is a default option. Using shady source for components is not a reason to complicate the design. 

However, as shady sources may be our only option these days, we could add a pad for goldpin header for programming Si5340. Then manufacturer can introduce appropriate programming action into the testing procedure (before assembling SOM).

jmatyas, 2022-06-28:
> Have you tried reprogramming Si5340 to use 1.8V?

Yup. I burned this configuration to its NVM. However it has not been yet tested with the bus voltage pulled up to the 1.8 V.

> However, as shady sources may be our only option these days, we could add a pad for goldpin header for programming Si5340. Then manufacturer can introduce appropriate programming action into the testing procedure (before assembling SOM).

That makes sense, but bear in mind, that pull-up resistors on this bus are placed on the Fast Sevro carrier, not on SoM. What's more the 3.3 V power won't start, if it doesn't detect enable signal,  which in this case comes from SoM.

jmatyas, 2022-07-06:
> > Have you tried reprogramming Si5340 to use 1.8V?
> 
> Yup. I burned this configuration to its NVM. However it has not been yet tested with the bus voltage pulled up to the 1.8 V.

I tested the I2C connection on hardware with SoM mounted. Works like charm

kaolpr, 2024-06-14:
It seems that Si5340 is more available now and we can assume it will be set to defaults. However, I suggest we add test points for the purpose of reprogramming in case of someone needs to recover from erronous programming.

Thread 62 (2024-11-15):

sinara-hw/Fast_Servo #62: DAC Output Discrepency between Channels

linuswck, 2024-11-15:
# Description
DAC Output 0 and DAC Output 1 should have the same output voltage range but it is not. I suspect there is something wrong with the DAC AFE Stage.

The prototype board we received has the ADA4930-2YCPZ used as a differential to single end converter but the differential to single end operation is not specified in the OpAmp datasheet. 
[image]

# Point of Measurement
Measurements are taken with Fluke 87V at the AD9117-2 output resistors and DAC SMA Output Port.
[image]
[image]

# Measurement Result
|     | AD9117-2 Output | DAC SMA Output | Unsigned Data |
| -------- | ------- | ------- | ------- |
| Channel 0 | -427.8mV   | -157mV | 0x0000 |
| Channel 1 | -426.1mV   |-163mV  |  0x0000 |
| Channel 0 | 429.2mV    | 258mV  | 0x3FFF|
| Channel 1 | 424.3mV    |323mV   |  0x3FFF |

Note: AD9117-2 DAC is set to received unsigned data before the measurement is taken.

gkasprow, 2024-11-15:
Every opamp is specified for diff to SE conversion.

mkiepiela, 2025-02-05:
This problem is caused by the DAC AFE oscillations pointed out in https://github.com/sinara-hw/Fast_Servo/issues/64 and after fixing this issue, the output values are like:

|     | AD9117-2 Output | DAC SMA Output | Unsigned Data |
| -------- | ------- | ------- | ------- |
| Channel 0 | -424,27 mV  | -271.54 mV | 0x0000 |
| Channel 1 | -422,87 mV  |-272.62 mV  |  0x0000 |
| Channel 0 | -0,06 mV   | 31.19 mV  | 0x2000|
| Channel 1 | 0,02 mV   |29.15 mV   |  0x2000 |
| Channel 0 | 424,4 mV   | 333.60 mV  | 0x3FFF|
| Channel 1 | 422,9 mV   |330.67 mV   |  0x3FFF |

Now the discrepancy between the channels seems to be correct and acceptable.

Note: DC measurements taken with Uni-T UT181A.

---
[image]

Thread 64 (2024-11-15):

sinara-hw/Fast_Servo #64: DAC Output Noise Coupling

linuswck, 2024-11-15:
# Description
When I connect the DAC Output 0 to an oscilloscope and I always see a high frequency sin wave being coupled to the DAC output SMA port. This high frequency sin wave exists even when the fast servo is powered up without the SD Card installed (so nothing is initialized). I am not sure if a board issue or a measurement problem.
[image]

# Connection Topology
Fast Servo DAC Output Port 0 -> SMA - to - SMA Cable -> SMA - to - BNC Adapter -> Oscilloscope BNC Port

# Other Info
Fast servo is installed inside a crate.
I tried powering it via PoE and power jack. The output noise makes no differences.
I have tested GND continuity between fast servo's and the SMA cable's, adapter's GND.
Oscilloscope Input Bandwidth is set to Full. This sin wave is still visible even after setting bandwidth to 20MHz.

mkiepiela, 2025-02-05:
Oscillations in the outputs come from an unstable amplifier in the DAC AFE.

This is caused by the parasitic inductance of the feedback capacitor and PCB tracks, as well as the parasitic capacitance in the summing node (amplifier inputs). This creates a filter pole and leads to excitation of the circuit.

When the feedback capacitors are removed, the oscillations disappear.
When they are mounted, the oscillation frequency is about 770-790 MHz (depends on the channel).

[image]

Experimentally, I added inductance to the feedback capacitors (soldering them on pieces of wire), expecting this to increase the problem (lowering the oscillation frequency).

[image]

The oscillation frequency decreased from 790 MHz to 600 MHz (green channel in the figures).

[image]

I'm going to test it with low ESL RF capacitors and update this topic.

Recommendations:
- use of RF capacitors with low ESL, preferably in smaller cases
- improved PCB layout (shorter and wider tracks and GND cutouts under the capacitor pads)

I am not closing this topic until the recommendations are implemented in the new revision.

---
[image]

linuswck, 2025-02-19:
I am testing the DAC AFE circuit using the EVAL-FDA-2 evaluation board to verify whether PCB layout has any contribution to the oscillation. The ADA4930-2 outputs oscillate even with RF capacitor being installed.

# Test Setup
RF Capacitor: 33pF (P/N: 06031U330FAT2A)
All Resistors used are 0402 0.1% tol.
Rf: 499ohm
Rg: 348ohm

Both IN-, IN+ are tied to GND via a 20ohm resistor
Both OUT-, OUT+ has a 0R series resistor installed.
Both Vocm are tied to GND.

+2.5V Power Source: TPS7A4901
-2.5V Power Source:  TPS7A3001

PD_n pins are tied to VS+.

Waveform are measured at OUT2+.

# Waveform
OUT1+ and OUT2+ have the same shape of waveform.
[image]
(Note: The scope used only has 500MHz bandwidth.)

linuswck, 2025-02-20:
OpAmp can be stabilized by adding an input capacitor across opamp inputs. But, the minimum value required depends on the PCB layout.
[image]

# Test Setup on  EVAL-FDA-2
This is tested on the EVAL-FDA-2 board. Same setup as previous reply. Both inputs are GND-ed via a 20ohm resistor. 
I tested the following values of capacitors.
| P/N | Value | Std deviation| Stable or Not? |
| -----| ------ | --------------------- | ---------------- |
| KGQ05FCG1H120FH | 0402 12pF +-1% | 7.61mV | Unstable |
| KGQ05FCG1H200FH | 0402 20pF +-1% | 6.25mV | Unstable |
| 06031U330FAT2A | 0603 33pF +-1% | 242.9uV | Stable |
| 06031U470JAT2A | 0603 47pF +-1% | 245.7uV | Stable |
| GRM188R71H221KA01D | 0603 220pF +-5% | 249.5uV | Stable |
(Note: Only 220pF capacitor is not RF capacitor)

### Waveforms
Pink Waveform is connected to OUT2+, which does not have 33pF feedback capacitor installed.
Green Waveform is connected to OUT1+, which is the DUT.

#### 0402 20pF +-1%
[image]

#### 0603 220pF+-1%
[image]

# Test Setup on the Fast-Servo
| P/N | Value | Std deviation | Stable or Not? |
| -----| ------ | --------------------- | ---------------- |
| 06031U330FAT2A | 0603 33pF +-1% | 3.51mV | Unstable |
| 06031U470JAT2A | 0603 47pF +-1% | 3.99mV | Unstable |
| 06031U680FAT2A | 0603 68pF +-1% | 1.31mV | Unstable |
| 06031U330FAT2A + 06031U680FAT2A | 0603 33pF + 68pF +-1% | 523uV | Stable |
| 06031U330FAT2A + 06031U680FAT2A | 0603 68pF + 33pF + 68pF +-1% | 503uV | Stable |
Note: Test Results are done on DAC1 Output

### Waveforms
Green Waveform is connected to Fast-servo Outputs.

#### 0603 33pF +-1%
[image]

#### 0603 68pF + 33pF + 68pF +-1% DAC1 Output
[image]

# Discussion
The added input capacitor shapes the noise gain of the FDA as discussed by this [app note from Ti] (https://www.ti.com/lit/an/slyt733/slyt733.pdf?ts=1740041287236&ref_url=https%253A%252F%252Fwww.google.com%252F). 
(Other useful forum post: https://e2e.ti.com/support/amplifiers-group/amplifiers/f/amplifiers-forum/664978/why-is-this-differential-mfb-lowpass-filter-oscillating)

As suggested by the ADA4930 datasheet(Layout Grounding and Bypassing section), Stray transmission line capacitance + package capacitance does contributes to the oscillation but as suggested by the EVAL-FDA-2 test result, a input capacitor is needed to stabilize the opamp. I think we should use 0402 resistor and (RF) capacitor for the FDA feedback path.

I think the DAC output is still very noisy compared to the DAC output range and 14 bit resolution. Should we build MFB differential low pass filter or add some kinds of filtering behind the DAC output?

linuswck, 2025-02-20:
Here is the output noise spectrum of DAC OUT1 on Fast Servo
Equipment: Keysight N9020A Signal Analyzer

0-1MHz Range
[image]

0-50MHz Range
[image]

0-500MHz Range
[image]

linuswck, 2025-02-21:
@gkasprow any thoughts?

linuswck, 2025-03-04:
> Maybe add a few ohm isolation resistors. 5Ohm or so

I think that is more likely a cable related issue. That's some unknown brand-ed cable. I tried cable that is fully specified. It works fine.

linuswck, 2025-03-04:
@gkasprow 
I know that ADA4930 should be one of the ADI FDA with lowest noise. But, I think its noise spec is only achievable when its differential output is used differentially? Particularly, the common mode noise is high as we can see from the measurement I took with the official evaluation board earlier.

[image]
C4: OUT1_P | C1: OUT1_N

I took the measurement again on the evaluation board with the same setup. We do not have any high bandwidth differential probe so the best I can do is to minus the both channels' readings digitally on the scope. But, we can still observe that generally OUTP and OUTN exhibits a significant amount common noise.

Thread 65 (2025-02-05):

sinara-hw/Fast_Servo #65: Incorrect DAC AFE Output Range

linuswck, 2025-02-05:
From #5, the DAC AFE Output Range is expected to be +-1V (Differential output) or +- 0.5V (Single-Ended output)

However, AD9117-2 output is Unipolar: 0 - IoutFS. (Configured as 0 - 20mA) and  the simulation assumed the AD9117-2 to be bipolar output with its output range as -20mA - 20mA. This causes the output range to be halved.

In other words, the current DAC AFE Output Range is +-0.5V(Differential output) or +- 0.25V (Single-Ended output)

mkiepiela, 2025-02-13:
The ~30 mV offset in output voltage range is due to the type of amplifier used in the AFE.

ADA4930 is differential output amplifier optimized for driving ADC with 0.9V common mode voltage.
The output common mode voltage is set by Vocm input (in FastServo tied to GND).

The offset voltage between Vocm pin and actual output common mode voltage is specified in datasheet for Vocm = 0.9V (assuming single +5 V supply).

[image]

1. In FastServo, only one (positive) of the differential outputs is used as a single ended output reffered to ground. 
This means that the Vocm offset adds to the output signal and is a source of asymmetry in the output voltage range.

2. Since ADA4930 is powered by +/-2.5 V and the Vocm pin is tied to GND, it is 2.5 V above the negative supply voltage. This is even outside the range specified in the datasheet (0.5 - 2.3 V above the negative supply). For this reason, the observed common mode offset (effectively a shift in the output signal range) is much higher than that specified for Vocm = 0.9 V (-25 - +15 mV, typically +0.35 mV).

As an exercise, I changed the positive and negative supply voltage values to move Vocm closer to the negative supply voltage.
I then measured the output signal (Vocm offset) for the DACs set at mid-range (0x2000, expected output signal value of 0 V). Vocm offset decreased as expected.

| Vs- [V] | Vs+ [V] | Vocm (for both DAC channels) |
|---|---|---|
| -2.5 | +2.5 | 28-30 mV |
| -2 | +3 | ~20 mV |
| -1.22 | +3 | 15-18 mV |
| -1.22 | +3.73 | 7-10 mV |

linuswck, 2025-02-20:
I think 28mV offset voltage is a little bit too much for such small output range. AD9117-2 Dac actually has a AUXDAC (one for each channel) that we can use. Or we can use a resistor divider to trim the offset?

linuswck, 2025-02-20:
I think the original designer assumed the OUTP and OUTN of the DAC could generate -ve output voltage but AD9117-2 output is [unipolar](https://ez.analog.com/data_converters/high-speed_dacs/f/q-a/22556/ad9116/167562). 

[image]

On fast-servo at OUT_P / OUT_N pin, using up the full 0-20mA current range, you can only generate a sin wave centered at 200mV with 200mV amplitude (200mV +-200mV), which is halved the range on what the simulation suggested. This can explain why the output is about halved.
Note: The extra small gain is contributed by the input impedance of the Dac AFE circuit, which can be eliminated by setting a Dac registers.

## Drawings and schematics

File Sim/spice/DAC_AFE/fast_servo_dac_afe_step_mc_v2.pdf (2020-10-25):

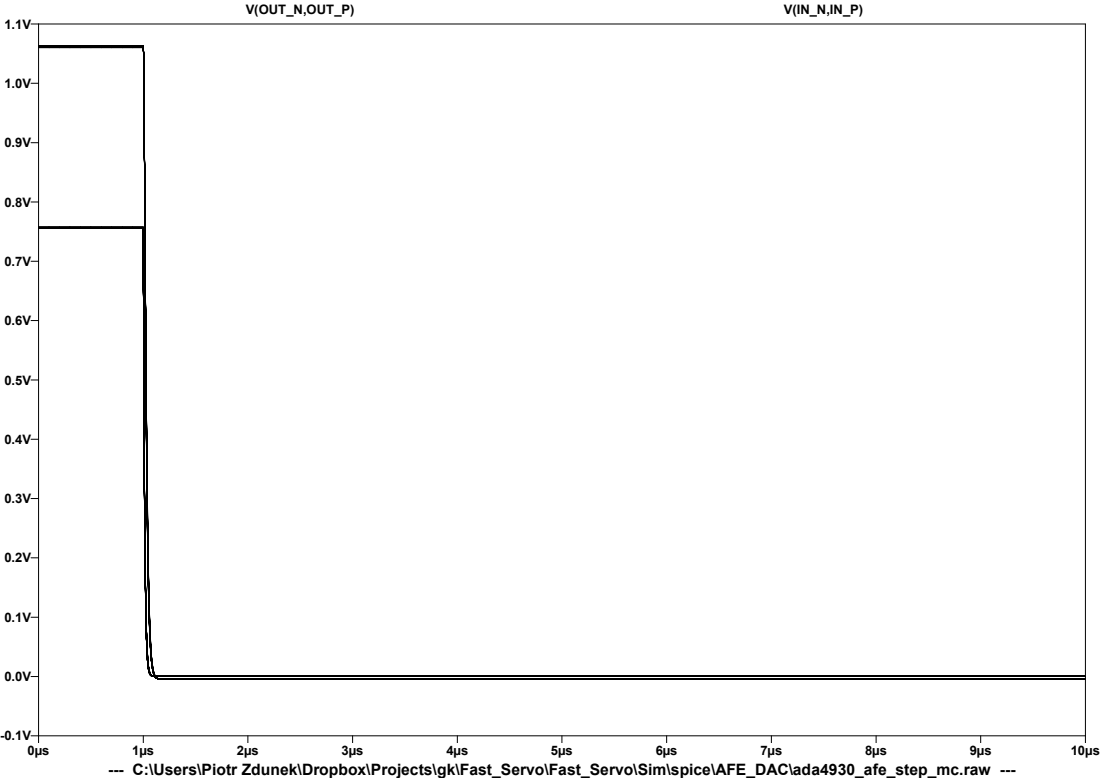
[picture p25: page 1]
V(OUT_N,OUT_P)

--- C:\Users\Piotr Zdunek\Dropbox\Projects\gk\Fast_Servo\Fast_Servo\Sim\spice\AFE_DAC\ada4930_afe_step_mc.raw ---

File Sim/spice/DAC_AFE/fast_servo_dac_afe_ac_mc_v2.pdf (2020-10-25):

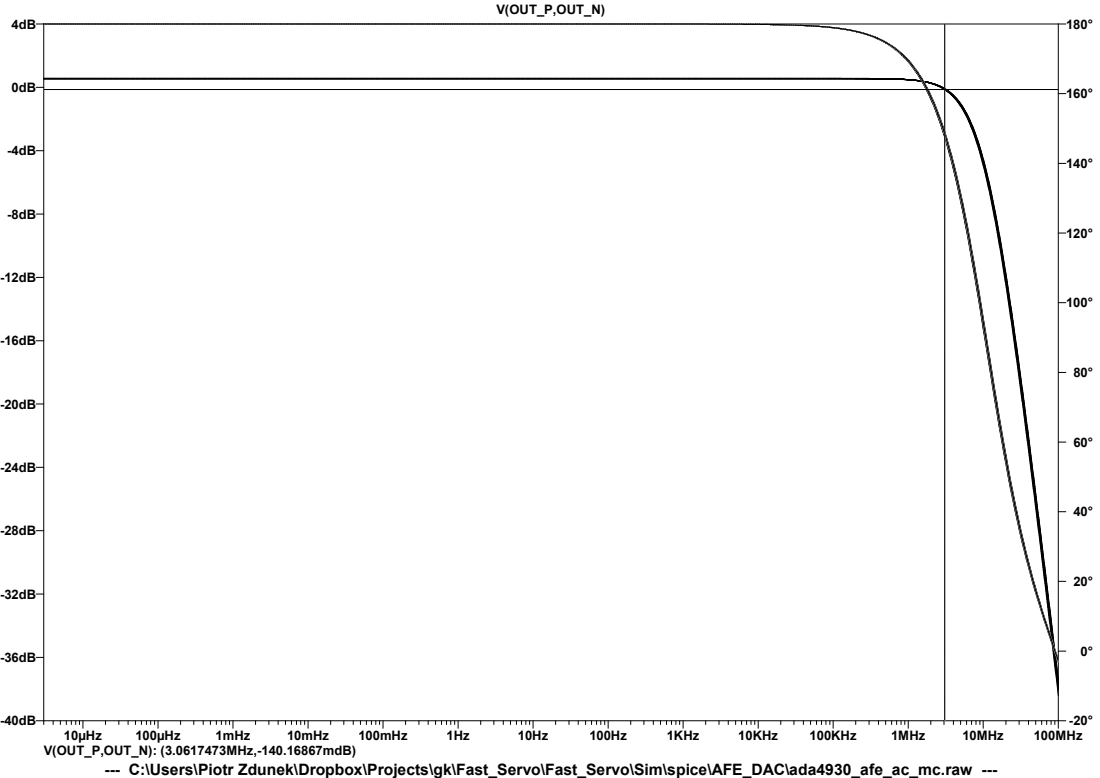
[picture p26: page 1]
10µHz; 100µHz; 1mHz; 10mHz; 100mHz; 1KHz; 10KHz; 100KHz; 1MHz; 10MHz; 100MHz; V(OUT_P,OUT_N); V(OUT_P,OUT_N): (3.0617473MHz,-140.16867mdB)

--- C:\Users\Piotr Zdunek\Dropbox\Projects\gk\Fast_Servo\Fast_Servo\Sim\spice\AFE_DAC\ada4930_afe_ac_mc.raw ---

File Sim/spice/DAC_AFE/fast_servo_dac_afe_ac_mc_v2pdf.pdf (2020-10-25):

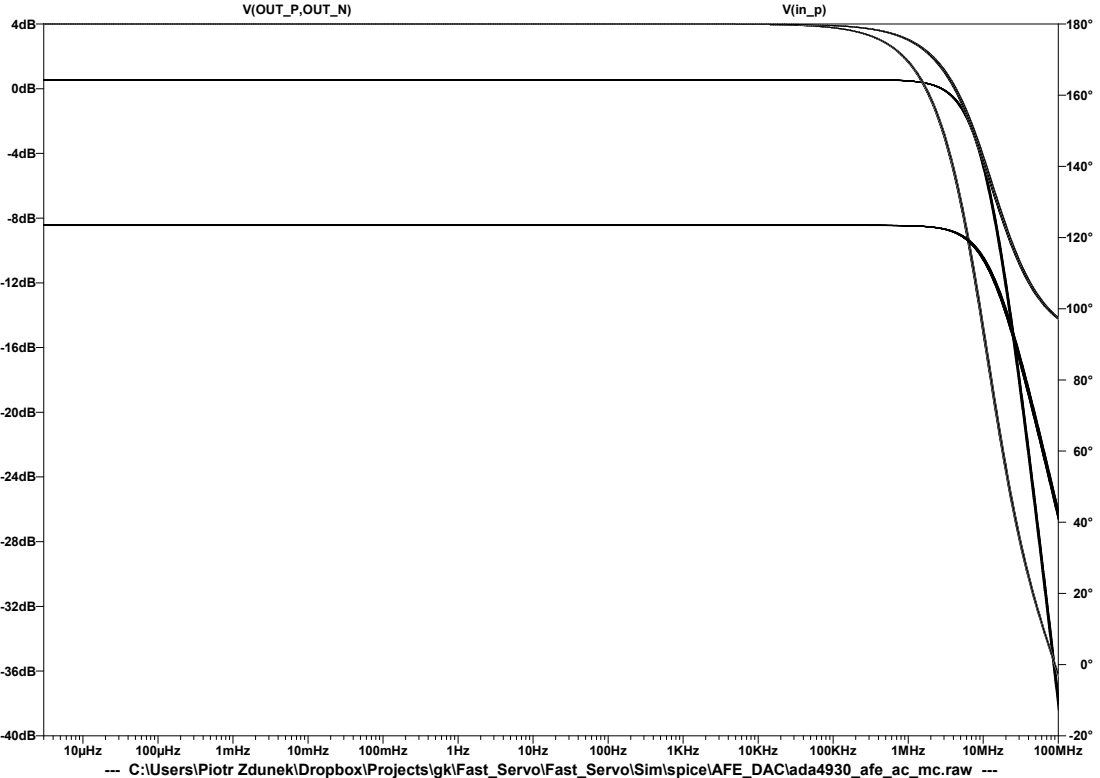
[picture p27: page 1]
10µHz; 100µHz; 1mHz; 10mHz; 100mHz; 1KHz; 10KHz; 100KHz; 1MHz; 10MHz; 100MHz; V(OUT_P,OUT_N)

--- C:\Users\Piotr Zdunek\Dropbox\Projects\gk\Fast_Servo\Fast_Servo\Sim\spice\AFE_DAC\ada4930_afe_ac_mc.raw ---

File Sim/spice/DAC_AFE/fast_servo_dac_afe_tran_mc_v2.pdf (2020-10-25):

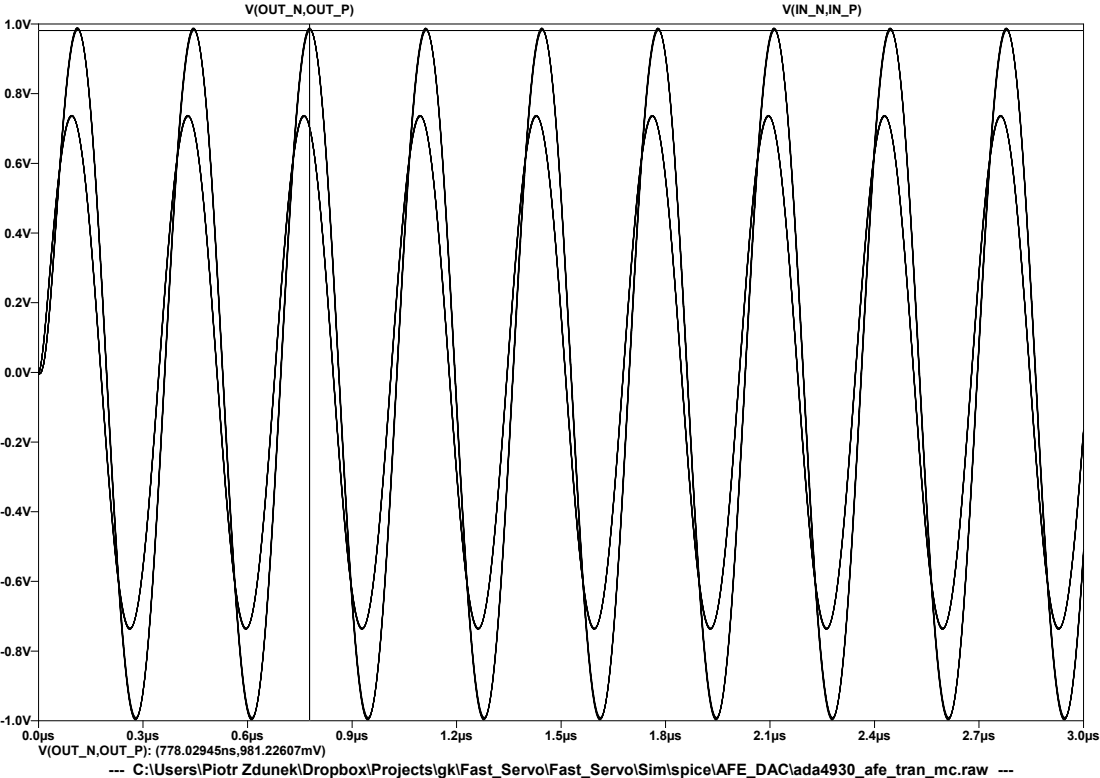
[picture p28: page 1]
V(OUT_N,OUT_P); V(OUT_N,OUT_P): (778.02945ns,981.22607mV)

--- C:\Users\Piotr Zdunek\Dropbox\Projects\gk\Fast_Servo\Fast_Servo\Sim\spice\AFE_DAC\ada4930_afe_tran_mc.raw ---

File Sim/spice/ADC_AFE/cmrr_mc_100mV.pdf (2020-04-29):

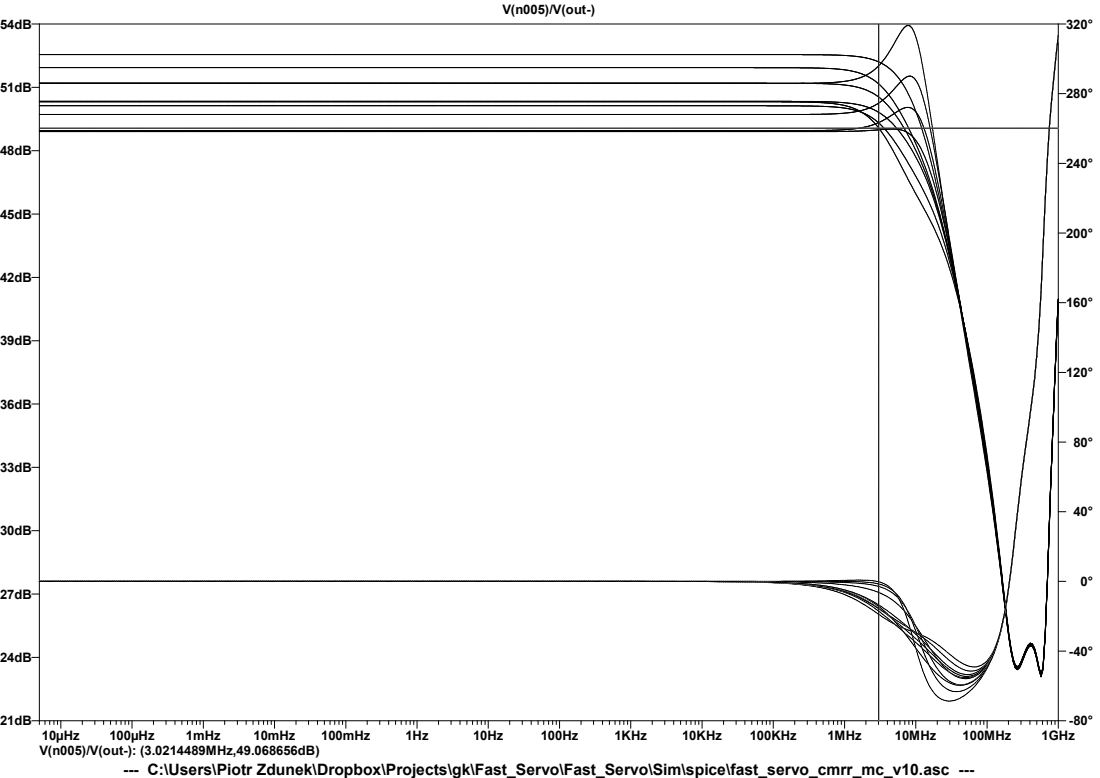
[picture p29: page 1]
10µHz; 100µHz; 1mHz; 10mHz; 100mHz; 1KHz; 10KHz; 100KHz; 1MHz; 10MHz; 100MHz; 1GHz; V(n005)/V(out-); V(n005)/V(out-): (3.0214489MHz,49.068656dB)

--- C:\Users\Piotr Zdunek\Dropbox\Projects\gk\Fast_Servo\Fast_Servo\Sim\spice\fast_servo_cmrr_mc_v10.asc ---

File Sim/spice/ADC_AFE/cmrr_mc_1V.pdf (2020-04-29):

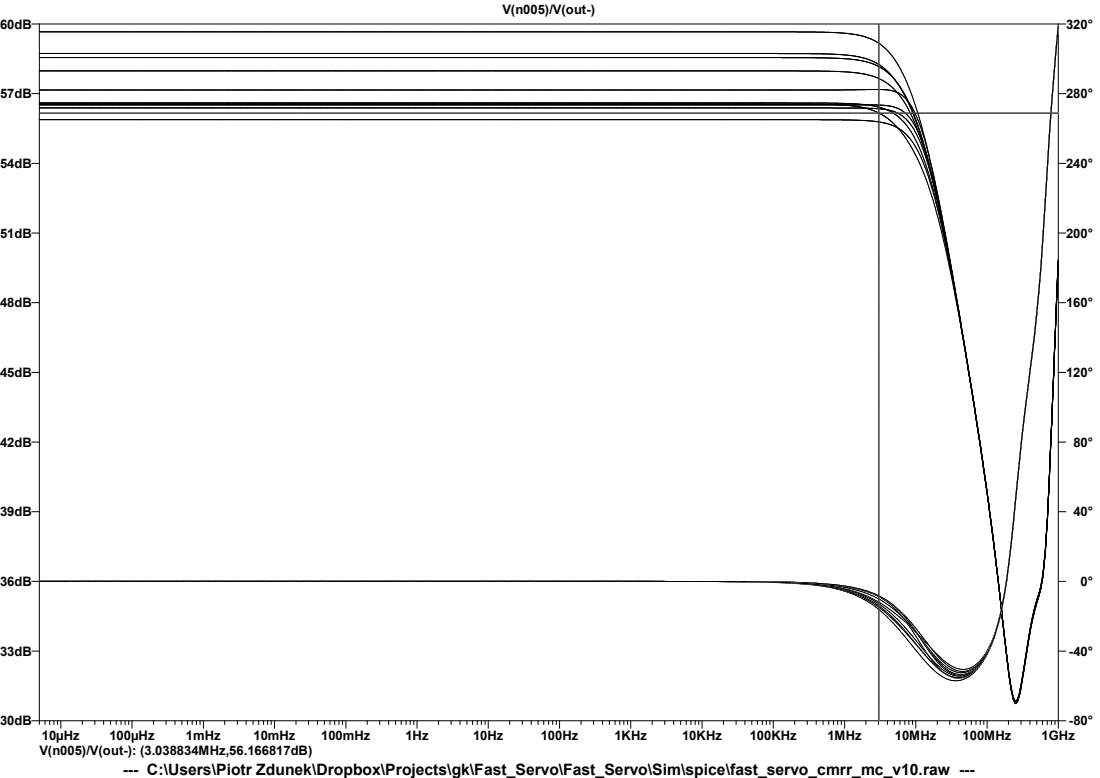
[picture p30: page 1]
10µHz; 100µHz; 1mHz; 10mHz; 100mHz; 1KHz; 10KHz; 100KHz; 1MHz; 10MHz; 100MHz; 1GHz; V(n005)/V(out-); V(n005)/V(out-): (3.038834MHz,56.166817dB)

--- C:\Users\Piotr Zdunek\Dropbox\Projects\gk\Fast_Servo\Fast_Servo\Sim\spice\fast_servo_cmrr_mc_v10.raw ---

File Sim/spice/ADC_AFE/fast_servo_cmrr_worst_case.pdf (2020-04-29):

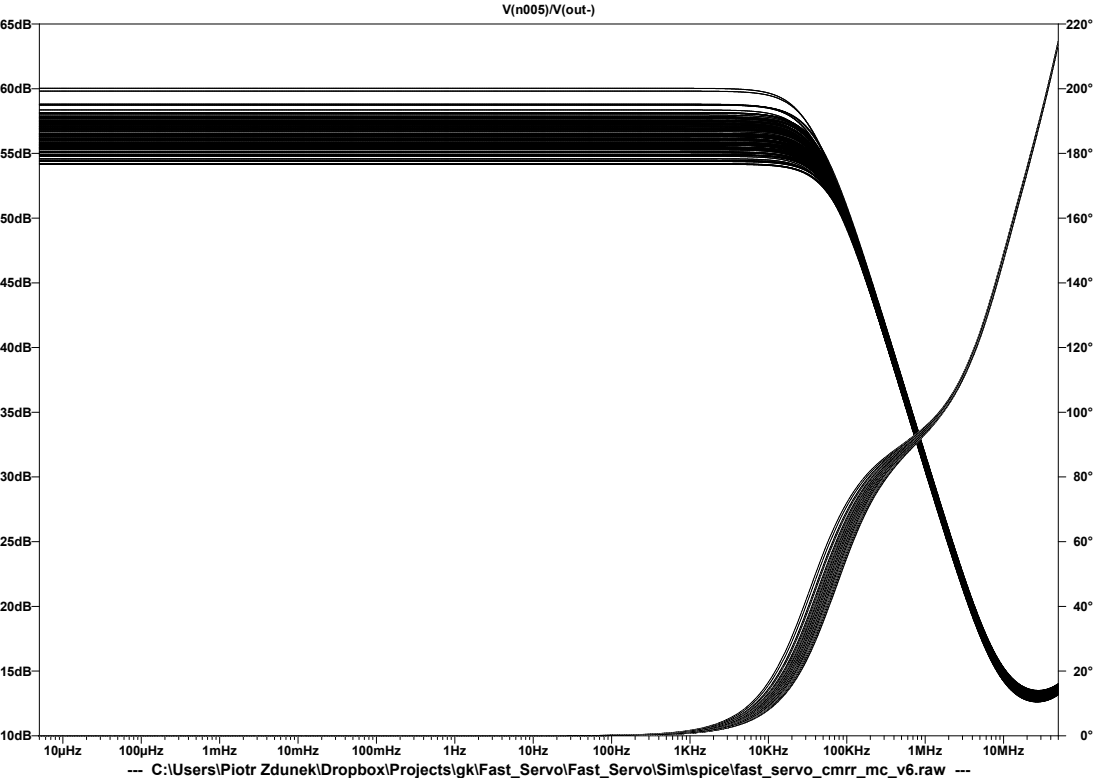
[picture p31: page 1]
10µHz; 100µHz; 1mHz; 10mHz; 100mHz; 1KHz; 10KHz; 100KHz; 1MHz; 10MHz; V(n005)/V(out-)

--- C:\Users\Piotr Zdunek\Dropbox\Projects\gk\Fast_Servo\Fast_Servo\Sim\spice\fast_servo_cmrr_mc_v6.raw ---

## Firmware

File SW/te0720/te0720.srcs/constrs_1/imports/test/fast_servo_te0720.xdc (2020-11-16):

# JM1

set_property PACKAGE_PIN C22  [get_ports HRTIM_CHA1             ]
set_property PACKAGE_PIN H22  [get_ports HRTIM_CHE1             ]
set_property PACKAGE_PIN A22  [get_ports HRTIM_CHA2             ]
set_property PACKAGE_PIN D22  [get_ports HRTIM_CHE2             ]
set_property PACKAGE_PIN G22  [get_ports DI1                    ]
set_property PACKAGE_PIN A18  [get_ports DI0                    ]
set_property PACKAGE_PIN B21  [get_ports LPTIM2_OUT             ]
set_property PACKAGE_PIN D16  [get_ports FP_LED_0               ]
set_property PACKAGE_PIN A21  [get_ports FP_LED_1               ]
set_property PACKAGE_PIN B15  [get_ports FP_LED_2               ]
set_property PACKAGE_PIN A16  [get_ports FP_LED_3               ]
set_property PACKAGE_PIN B17  [get_ports SPI1_MOSI              ]
set_property PACKAGE_PIN B16  [get_ports SPI1_MISO              ]
set_property PACKAGE_PIN E20  [get_ports SPI1_NSS               ]
set_property PACKAGE_PIN B22  [get_ports QSPI_NCS               ]
set_property PACKAGE_PIN G20  [get_ports QSPI_CLK               ]
set_property PACKAGE_PIN G21  [get_ports {QSPI_IO[0]}           ]
set_property PACKAGE_PIN D21  [get_ports {QSPI_IO[1]}           ]
set_property PACKAGE_PIN E21  [get_ports {QSPI_IO[2]}           ]
set_property PACKAGE_PIN B20  [get_ports {QSPI_IO[3]}           ]
set_property PACKAGE_PIN E19  [get_ports SPI1_SCK               ]
set_property PACKAGE_PIN B19  [get_ports CLK_100M               ]
set_property PACKAGE_PIN D18  [get_ports ADC_AUX_DOUTA          ]
set_property PACKAGE_PIN C17  [get_ports ADC_AUX_DOUTB          ]
set_property PACKAGE_PIN C20  [get_ports LED3                   ]
set_property PACKAGE_PIN D20  [get_ports LED2                   ]
set_property PACKAGE_PIN G16  [get_ports LED1                   ]
set_property PACKAGE_PIN F22  [get_ports I2C1_SCL               ]
set_property PACKAGE_PIN C18  [get_ports I2C1_SDA               ]
set_property PACKAGE_PIN G15  [get_ports UART4_TX               ]
set_property PACKAGE_PIN E18  [get_ports DAC_AUX_BIN            ]
set_property PACKAGE_PIN D15  [get_ports ADC_AUX_SGL            ]
set_property PACKAGE_PIN F21  [get_ports ADC_AUX_A0             ]
set_property PACKAGE_PIN G19  [get_ports ADC_AUX_A1             ]
set_property PACKAGE_PIN F19  [get_ports ADC_AUX_A2             ]
set_property PACKAGE_PIN F17  [get_ports DAC_AUX_nCLR           ]
set_property PACKAGE_PIN G17  [get_ports ADC_AUX_RANGE          ]
set_property PACKAGE_PIN E16  [get_ports DAC_AUX_nLDAC          ]
set_property PACKAGE_PIN F16  [get_ports ADC_AUX_SCLK           ]
set_property PACKAGE_PIN C19  [get_ports ADC_AUX_nCS            ]
set_property PACKAGE_PIN H20  [get_ports DAC_AUX_SDIN           ]
set_property PACKAGE_PIN H19  [get_ports DAC_AUX_SDO            ]
set_property PACKAGE_PIN F18  [get_ports DAC_AUX_nSYNC          ]
set_property PACKAGE_PIN E15  [get_ports DAC_AUX_SCLK           ]
set_property PACKAGE_PIN A17  [get_ports ETH_LED1               ]
set_property PACKAGE_PIN A19  [get_ports ETH_LED2               ]
set_property PACKAGE_PIN C15  [get_ports ADC_AFE_CH2_GAIN_X10   ]
set_property PACKAGE_PIN D17  [get_ports ADC_AFE_CH1_GAIN_X10   ]

set_property IOSTANDARD LVCMOS33 [get_ports HRTIM_CHA1          ]      
set_property IOSTANDARD LVCMOS33 [get_ports HRTIM_CHE1          ]      
set_property IOSTANDARD LVCMOS33 [get_ports HRTIM_CHA2          ]      
set_property IOSTANDARD LVCMOS33 [get_ports HRTIM_CHE2          ]      
set_property IOSTANDARD LVCMOS33 [get_ports DI1                 ]      
set_property IOSTANDARD LVCMOS33 [get_ports DI0                 ]      
set_property IOSTANDARD LVCMOS33 [get_ports LPTIM2_OUT          ]      
set_property IOSTANDARD LVCMOS33 [get_ports FP_LED_0            ]      
set_property IOSTANDARD LVCMOS33 [get_ports FP_LED_1            ]      
set_property IOSTANDARD LVCMOS33 [get_ports FP_LED_2            ]      
set_property IOSTANDARD LVCMOS33 [get_ports FP_LED_3            ]      
set_property IOSTANDARD LVCMOS33 [get_ports SPI1_MOSI           ]      
set_property IOSTANDARD LVCMOS33 [get_ports SPI1_MISO           ]      
set_property IOSTANDARD LVCMOS33 [get_ports SPI1_NSS            ]      
set_property IOSTANDARD LVCMOS33 [get_ports QSPI_NCS            ]      
set_property IOSTANDARD LVCMOS33 [get_ports QSPI_CLK            ]      
set_property IOSTANDARD LVCMOS33 [get_ports {QSPI_IO[0]}        ]      
set_property IOSTANDARD LVCMOS33 [get_ports {QSPI_IO[1]}        ]      
set_property IOSTANDARD LVCMOS33 [get_ports {QSPI_IO[2]}        ]      
set_property IOSTANDARD LVCMOS33 [get_ports {QSPI_IO[3]}        ]      
set_property IOSTANDARD LVCMOS33 [get_ports SPI1_SCK            ]      
set_property IOSTANDARD LVCMOS33 [get_ports CLK_100M            ]      
set_property IOSTANDARD LVCMOS33 [get_ports ADC_AUX_DOUTA       ]      
set_property IOSTANDARD LVCMOS33 [get_ports ADC_AUX_DOUTB       ]      
set_property IOSTANDARD LVCMOS33 [get_ports LED3                ]      
set_property IOSTANDARD LVCMOS33 [get_ports LED2                ]      
set_property IOSTANDARD LVCMOS33 [get_ports LED1                ]      
set_property IOSTANDARD LVCMOS33 [get_ports I2C1_SCL            ]      
set_property IOSTANDARD LVCMOS33 [get_ports I2C1_SDA            ]      
set_property IOSTANDARD LVCMOS33 [get_ports UART4_TX            ]      
set_property IOSTANDARD LVCMOS33 [get_ports DAC_AUX_BIN         ]      
set_property IOSTANDARD LVCMOS33 [get_ports ADC_AUX_SGL         ]      
set_property IOSTANDARD LVCMOS33 [get_ports ADC_AUX_A0          ]      
set_property IOSTANDARD LVCMOS33 [get_ports ADC_AUX_A1          ]      
set_property IOSTANDARD LVCMOS33 [get_ports ADC_AUX_A2          ]      
set_property IOSTANDARD LVCMOS33 [get_ports DAC_AUX_nCLR        ]      
set_property IOSTANDARD LVCMOS33 [get_ports ADC_AUX_RANGE       ]      
set_property IOSTANDARD LVCMOS33 [get_ports DAC_AUX_nLDAC       ]      
set_property IOSTANDARD LVCMOS33 [get_ports ADC_AUX_SCLK        ]      
set_property IOSTANDARD LVCMOS33 [get_ports ADC_AUX_nCS         ]      
set_property IOSTANDARD LVCMOS33 [get_ports DAC_AUX_SDIN        ]      
set_property IOSTANDARD LVCMOS33 [get_ports DAC_AUX_SDO         ]      
set_property IOSTANDARD LVCMOS33 [get_ports DAC_AUX_nSYNC       ]      
set_property IOSTANDARD LVCMOS33 [get_ports DAC_AUX_SCLK        ]      
set_property IOSTANDARD LVCMOS33 [get_ports ETH_LED1            ]      
set_property IOSTANDARD LVCMOS33 [get_ports ETH_LED2            ]      
set_property IOSTANDARD LVCMOS33 [get_ports ADC_AFE_CH2_GAIN_X10]      
set_property IOSTANDARD LVCMOS33 [get_ports ADC_AFE_CH1_GAIN_X10]      

# JM2

set_property PACKAGE_PIN   AA22   [get_ports DAC_nCS            ]
set_property PACKAGE_PIN   W20    [get_ports SI5340_SCL         ]
set_property PACKAGE_PIN   AB22   [get_ports DAC_SDIO           ]
set_property PACKAGE_PIN   W21    [get_ports SI5340_SDA         ]
set_property PACKAGE_PIN   AA21   [get_ports SI5340_LOS_XAXBb   ]
set_property PACKAGE_PIN   AB21   [get_ports Si5340_nLOL        ]
set_property PACKAGE_PIN   W17    [get_ports FPGA_CLK1_CLK_N    ]
set_property PACKAGE_PIN   Y19    [get_ports SI5340_nINTR       ]
set_property PACKAGE_PIN   W18    [get_ports FPGA_CLK1_CLK_P    ]
set_property PACKAGE_PIN   AA19   [get_ports DAC_SCLK           ]
set_property PACKAGE_PIN   W16    [get_ports SI5340_nRST        ]
set_property PACKAGE_PIN   Y18    [get_ports DAC_AFE_CH1_nPD    ]
set_property PACKAGE_PIN   Y16    [get_ports AT_EVENT           ]
set_property PACKAGE_PIN   AA18   [get_ports DAC_AFE_CH2_nPD    ]
set_property PACKAGE_PIN   AA17   [get_ports ADC_CS             ]
set_property PACKAGE_PIN   AB17   [get_ports ADC_SCK            ]
set_property PACKAGE_PIN   AA16   [get_ports ADC_SDI            ]
set_property PACKAGE_PIN   AB16   [get_ports ADC_SDO            ]
                                  
set_property IOSTANDARD  LVCMOS18   [get_ports DAC_nCS          ]
set_property IOSTANDARD  LVCMOS18   [get_ports SI5340_SCL       ] 
set_property IOSTANDARD  LVCMOS18   [get_ports DAC_SDIO         ] 
set_property IOSTANDARD  LVCMOS18   [get_ports SI5340_SDA       ] 
set_property IOSTANDARD  LVCMOS18   [get_ports SI5340_LOS_XAXBb ] 
set_property IOSTANDARD  LVCMOS18   [get_ports Si5340_nLOL      ] 
set_property IOSTANDARD  LVCMOS18   [get_ports FPGA_CLK1_CLK_N  ] 
set_property IOSTANDARD  LVCMOS18   [get_ports SI5340_nINTR     ] 
set_property IOSTANDARD  LVCMOS18   [get_ports FPGA_CLK1_CLK_P  ] 
set_property IOSTANDARD  LVCMOS18   [get_ports DAC_SCLK         ] 
set_property IOSTANDARD  LVCMOS18   [get_ports SI5340_nRST      ] 
set_property IOSTANDARD  LVCMOS18   [get_ports DAC_AFE_CH1_nPD  ] 
set_property IOSTANDARD  LVCMOS18   [get_ports AT_EVENT         ] 
set_property IOSTANDARD  LVCMOS18   [get_ports DAC_AFE_CH2_nPD  ] 
set_property IOSTANDARD  LVCMOS18   [get_ports ADC_CS           ] 
set_property IOSTANDARD  LVCMOS18   [get_ports ADC_SCK          ] 
set_property IOSTANDARD  LVCMOS18   [get_ports ADC_SDI          ] 
set_property IOSTANDARD  LVCMOS18   [get_ports ADC_SDO          ] 
 
set_property PACKAGE_PIN U11  [get_ports OUT1D_N     ]
set_property PACKAGE_PIN U12  [get_ports OUT1D_P     ]
set_property PACKAGE_PIN U10  [get_ports FR_P        ]
set_property PACKAGE_PIN U9   [get_ports FR_N        ]

set_property IOSTANDARD LVDS_25  [get_ports OUT1D_N  ]
set_property IOSTANDARD LVDS_25  [get_ports OUT1D_P  ]
set_property IOSTANDARD LVDS_25  [get_ports FR_P     ]
set_property IOSTANDARD LVDS_25  [get_ports FR_N     ]

set_property PACKAGE_PIN AB9     [get_ports OUT1A_P           ]	
set_property PACKAGE_PIN AB10    [get_ports OUT1A_N           ]
set_property PACKAGE_PIN AB11    [get_ports OUT1B_P           ]
set_property PACKAGE_PIN AA11    [get_ports OUT1B_N           ]
set_property PACKAGE_PIN AB12    [get_ports OUT1C_P           ]
set_property PACKAGE_PIN AA12    [get_ports OUT1C_N           ]
set_property PACKAGE_PIN V10     [get_ports OUT2A_P           ]
set_property PACKAGE_PIN V9      [get_ports OUT2A_N           ]
set_property PACKAGE_PIN Y6      [get_ports OUT2B_P	          ]
set_property PACKAGE_PIN Y5      [get_ports OUT2B_N           ]
set_property PACKAGE_PIN V12     [get_ports OUT2C_P           ]	
set_property PACKAGE_PIN W12     [get_ports OUT2C_N           ]	
set_property PACKAGE_PIN W10     [get_ports OUT2D_N           ]
set_property PACKAGE_PIN W11     [get_ports OUT2D_P           ]
set_property PACKAGE_PIN Y9      [get_ports DCO_P             ]
set_property PACKAGE_PIN Y8      [get_ports DCO_N             ]
set_property PACKAGE_PIN AA8     [get_ports CLK2_P            ]
set_property PACKAGE_PIN AA9     [get_ports CLK2_N            ]
set_property PACKAGE_PIN U4      [get_ports LVDS7_P           ]
set_property PACKAGE_PIN T4      [get_ports LVDS7_N           ]
set_property PACKAGE_PIN AB6     [get_ports LVDS6_P           ]
set_property PACKAGE_PIN AB7     [get_ports LVDS6_N           ]
set_property PACKAGE_PIN AA4     [get_ports LVDS5_P           ]
set_property PACKAGE_PIN Y4      [get_ports LVDS5_N           ]
set_property PACKAGE_PIN AB1     [get_ports LVDS4_P           ]
set_property PACKAGE_PIN AB2     [get_ports LVDS4_N           ]
set_property PACKAGE_PIN W7      [get_ports LVDS3_P           ]
set_property PACKAGE_PIN V7      [get_ports LVDS3_N           ]
set_property PACKAGE_PIN V4      [get_ports LVDS2_P           ]
set_property PACKAGE_PIN V5      [get_ports LVDS2_N           ]
set_property PACKAGE_PIN R6      [get_ports LVDS1_P           ]
set_property PACKAGE_PIN T6      [get_ports LVDS1_N           ]
set_property PACKAGE_PIN AA7     [get_ports LVDS0_P           ]
set_property PACKAGE_PIN AA6     [get_ports LVDS0_N           ]
set_property PACKAGE_PIN U6      [get_ports ADC_AFE_CH2_nSHDN ]
set_property PACKAGE_PIN U5      [get_ports ADC_AFE_CH1_nSHDN ]
set_property PACKAGE_PIN W8      [get_ports TERM_STAT0        ]
set_property PACKAGE_PIN V8      [get_ports TERM_STAT1        ]
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

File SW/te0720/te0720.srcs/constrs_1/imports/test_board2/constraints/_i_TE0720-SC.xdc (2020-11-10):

#
# Constraints for System controller support logic
#
set_property PACKAGE_PIN K16 [get_ports PL_pin_K16]
set_property PACKAGE_PIN K19 [get_ports PL_pin_K19]
set_property PACKAGE_PIN K20 [get_ports PL_pin_K20]
set_property PACKAGE_PIN L16 [get_ports PL_pin_L16]
set_property PACKAGE_PIN M15 [get_ports PL_pin_M15]
set_property PACKAGE_PIN N15 [get_ports PL_pin_N15]
set_property PACKAGE_PIN N22 [get_ports PL_pin_N22]
set_property PACKAGE_PIN P16 [get_ports PL_pin_P16]
set_property PACKAGE_PIN P22 [get_ports PL_pin_P22]

#
# If Bank 34 is not 3.3V Powered need change the IOSTANDARD
#
set_property IOSTANDARD LVCMOS18 [get_ports PL_pin_P22]
set_property IOSTANDARD LVCMOS18 [get_ports PL_pin_P16]
set_property IOSTANDARD LVCMOS18 [get_ports PL_pin_N22]
set_property IOSTANDARD LVCMOS18 [get_ports PL_pin_N15]
set_property IOSTANDARD LVCMOS18 [get_ports PL_pin_M15]
set_property IOSTANDARD LVCMOS18 [get_ports PL_pin_L16]
set_property IOSTANDARD LVCMOS18 [get_ports PL_pin_K20]
set_property IOSTANDARD LVCMOS18 [get_ports PL_pin_K19]
set_property IOSTANDARD LVCMOS18 [get_ports PL_pin_K16]

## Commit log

2020-01-07 Initial commit. Dummy Altium Designer project based on Stabilizer project. SoM TE7020 used from SpaceVPX project.
    [ADC.SchDoc, AUX_Analog_IO.SchDoc, CPU.SchDoc, DAC.SchDoc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]
2020-01-07 Moving PCB files to a separate folder.
    [ADC.SchDoc, AUX_Analog_IO.SchDoc, CPU.SchDoc, DAC.SchDoc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]
2020-03-29 Adding basic design with LTC2195 wrapper. A basis for future HDL simulation of readout. Updated some PCB schematics.
    [ADC.SchDoc, DAC.SchDoc, Fast_Servo.PrjPCB, Fast_Servo.schdoc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]
2020-03-30 Adding JTAG connector, Ethernet, SoM, Supply (based on Stabilizer) and SD CARD. Power supply for SD card needs to be determined.
    [AUX_CON.SchDoc, ETH_CON.SchDoc, Fast_Servo.PrjPCB, SD_CARD.SchDoc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]
2020-04-02 Updated SoM and SDCARD schematics.
    [SD_CARD.SchDoc, SoM.SchDoc]
2020-04-04 Update of simulation file and SD CARD schematics - used components from the library.
    [SD_CARD.SchDoc, TOP.SchDoc]
2020-04-05 Updated schematics - USB circuit. Updated ADC AFE simulation file.
    [Fast_Servo.PrjPCB, SoM.SchDoc, TOP.SchDoc, USB.SchDoc]
2020-04-05 Added CMRR simulation file for ADC AFE - not yet working. Updated schematics - added digital inputs to SoM, EEM connector and LEDs.
    [AUX_CON.SchDoc, Digital_Input.SchDoc, EEM_connector.SchDoc, Fast_Servo.PrjPCB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]
2020-04-29 Adding reports and updated schematics.
    [ADC.SchDoc, AUX_Analog_IO.SchDoc, DAC.SchDoc, Fast_Servo.PrjPCB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]
2020-04-29 Adding some schematics. Adding LTSpice simulation files.
    [ADC_AFE.SchDoc, DIO.SchDoc]
2020-06-05 Updated schematics. Draft version. Can be reviewed.
    [ADC.SchDoc, ADC_AFE.SchDoc, ADC_AUX.SchDoc, AUX_Analog_IO.SchDoc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]
2020-06-11 Updated schematics. Added P1V8 analog supply for ADC. Fixed errors.
    [ADC.SchDoc, ADC_AFE.SchDoc, ADC_AUX.SchDoc, AUX_Analog_IO.SchDoc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]
2020-06-13 Updated schematics. Changed the supply of the AD4817-2 in ADC AFE circuit to +/- 5V.
    [ADC.SchDoc, ADC_AFE.SchDoc, ADC_AUX.SchDoc, AUX_Analog_IO.SchDoc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]
2020-06-24 Updated schematics and started basic layout.
    [ADC.SchDoc, ADC_AFE.SchDoc, ADC_AUX.SchDoc, AUX_Analog_IO.SchDoc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]
2020-07-23 Schematic update. Basic layout, component placement.
    [ADC.SchDoc, ADC_AFE.SchDoc, DAC.SchDoc, DAC_AFE.SchDoc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]
2020-07-26 Minor updates in Power supply design. Changed NetTie to a jumper resistor for local analog ground separation. Changed PCB component placement for more optimal power supply design.
    [DAC.SchDoc, Fast_Servo.PrjPCB, PWR_P1V8A.SchDoc, PWR_P6V0.SchDoc]
2020-07-28 Updated schematics. Progressed layout.
    [ADC_AUX.SchDoc, AUX_Analog_IO.SchDoc, DAC_AUX.SchDoc, Fast_Servo.PrjPCB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]
2020-07-28 Minor updates. Removed deprecated note and set the image on eth con sheet to be embedded.
    [ETH_CON.SchDoc, Supply_Fast_Servo.SchDoc]
2020-08-06 Schematics update. Added SI5340 clock generation IC for ADC/DAC and FPGA. Updated the power supply section. P1V8A has a higher output current. P6V0 and N6V0 changed to P5V5 and N5V5 for better effici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
    [ADC.SchDoc, ADC_AFE.SchDoc, ADC_AUX.SchDoc, CLK_GEN.SchDoc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]
2020-08-06 Updated sheet numbers.
    [ADC.SchDoc, ADC_AFE.SchDoc, ADC_AUX.SchDoc, AUX_Analog_IO.SchDoc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]
2020-08-10 Clock generation IC schematic updated and the related schematics also. Updated Power supply. After P3V3 is up the signal is set on PoE to short the resistor limitting power. Signals on SoM were updat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
    [ADC.SchDoc, CLK_GEN.SchDoc, DAC.SchDoc, DAC_AFE.SchDoc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]
2020-08-24 Schematic update with 12V0A and -12V0A supplies for mezzanines. Modified the names of the signals for GPIO connectors. Updated names of schematics files to be more consistent.
    [ADC_AUX.SchDoc, AUX_Analog_IO.SchDoc, AUX_CON.SchDoc, CON_EEM.SchDoc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]
2020-08-31 Updated schematics to accomodate the use of mezzanine modules as per stabilizer. Updated power supply architecture. Updated signal connections so that different Trenz modules can be used. One bank wi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
    [ADC.SchDoc, ADC_AFE.SchDoc, ADC_AUX.SchDoc, AUX_Analog_IO.SchDoc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]
2020-08-31 Changed switch to jumper for Bank voltage selection.
    [SOM_JB2.SchDoc, TOP.SchDoc]
2020-09-10 Power supply updates to optimize placement. Updated placement on the PCB. Added 2.5V supply for Artix based Trenz modules. Added jumper to switch between 1.8V and 2.5V for the HP/HR bank in case of u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
    [ADC.SchDoc, ADC_AFE.SchDoc, CLK_GEN.SchDoc, CON_ETH.SchDoc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]
2020-09-19 Progressed routing. Schematic updates for easier routing.
    [ADC.SchDoc, CLK_GEN.SchDoc, CON_ETH.SchDoc, CON_MEZZANINE_GPIO_JTAG.SchDoc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]
2020-09-21 Updated PCB layout. Basic layout done. Updated schematics for easier layout. Fixed an error in ADC AFE schematics with a short.
    [ADC_AFE.SchDoc, PWR_P12V0A_N12V0A.SchDoc, SOM_JB1.SchDoc, SOM_JB2.SchDoc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]
2020-09-23 Updated schematics parameters, naming and numbering. Fixed DRCs in PCB after component unification.
    [ADC.SchDoc, ADC_AFE.SchDoc, ADC_AUX.SchDoc, AUX_Analog_IO.SchDoc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]
2020-09-30 Reannotated schematics. Performed power simulations using PDN analyzer. Changed LDO for 3.3V analog to a one with higher output current capability. Added additional decoupling capacitors to ADC VDD p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
    [ADC.SchDoc, ADC_AFE.SchDoc, ADC_AUX.SchDoc, CLK_GEN.SchDoc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]
2020-10-04 Found an issue in the design. Some pins in JB3 cannot be used, as in other Trenz modules they are occupied for MGT lines. Schematics are corrected. PCB to be updated. Found another issue with TERM si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
    [ADC_AFE.SchDoc, CLK_GEN.SchDoc, Fast_Servo.PrjPCB, LEDs.SchDoc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]
2020-10-07 Corrected the PCB and schematics.
    [DAC.SchDoc, SOM_JB2.SchDoc, SOM_JB3.SchDoc]
2020-10-10 Adding power simulations.
    [pins.csv, vcomp2id.csv, vias.csv, vpin2pin.csv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]
2020-10-19 Updated schematics and PCB layout. DRC to be done after PCB changes.
    [ADC.SchDoc, ADC_AFE.SchDoc, ADC_AUX.SchDoc, DAC.SchDoc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]
2020-10-20 Added archived vivado projects for TE0720, TE0715-15, TE0715-30 modules. Verified compatibility. Updated layout, added copper balancing pads, adjusted skew for differential pairs, verified the fittin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
    [Fast_Servo.PrjPCB]
2020-10-21 Updated PCB. Added missing harness files.
    [OK6010_DB.SCHLIB]
2020-10-23 Added testpoints to SPI of ADC and DAC. Updated net classes in the schematics.
    [ADC.SchDoc, CON_EEM.SchDoc, DAC.SchDoc, DAC_AFE.SchDoc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]
2020-10-24 Removed unnecessary TE0706 lib. Added whole TE0706 carrier project. Adding spreadsheets with different analysis:power supply, IO, ADC, DAC comparison.
    [FastServo DAC comparison.xlsx, FastServo ADC selection.xlsx, FastServo IO.xlsx, FastServo Power supply calculations.xlsx]
2020-10-25 Removed unnecessary files.
    [AUX_Analog_IO.SchDoc, CON_MEZZANINE_GPIO_JTAG.SchDoc, Digital_Input.SchDoc, PWR_N3V0.SchDoc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]
2020-10-25 Removing unnecessary files.
    [CON_MEZZANINE_ADC.SchDoc, EEM_connector.SchDoc, ETH_CON.SchDoc, Fast_Servo.PrjPCB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]
2020-10-25 Updated testpoints and fiducial to non-BOM components. Updated BOM setting.
    [ADC.SchDoc, DAC.SchDoc, DIGITAL_INPUTS.SchDoc, EEPROM.SchDoc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]
2020-11-10 Adding test board Vivado project.
2020-12-19 PCB/Schematic changes: 2 fiducials moved to BTM. Changed the DAC AFE to single ended. Negative output is terminated to ground. The same with the DAC outputs. SW Changes: removed generated files for I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
    [DAC_AFE.SchDoc, TOP.SchDoc]
2020-12-30 Fixed some issues: #14, #15, #16 # 17, #18, #19, #23, #24,
    [ADC.SchDoc, ADC_AFE.SchDoc, CON_MEZZANINE_ADC_DAC.SchDoc, CON_MEZZANINE_GPIO.SchDoc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]
2020-12-30 Fixed issues #25 and #26.
    [PWR_P2V5.SchDoc]
2020-12-31 Updated PCB layout to change the position of C103 on the input of the N5v5 DC/dC converter.
2021-01-01 Fixed changes in the PCB due to schematic update. One rule broke the DRC need to revert it.
    [DAC.SchDoc, PWR_P5V0A.SchDoc]
2021-01-01 Fixed layout of C22 so that it's more clear. Fixed width rules so that they do not generate so many violations.
    [ADC.SchDoc, PWR_P12V0A_N12V0A.SchDoc]
2021-01-01 Fixed width of net B2_1
    [ADC.SchDoc]
2021-01-01 Changed R42 and R56 resistors to 0603. Fixed width of some diff pairs on TOP and BTM to 0.16mm.
    [ADC_AFE.SchDoc]
2021-01-02 Fixed L4 GND plane. Fixed mounting holes for SoM - connected to ground.
    [TOP.SchDoc]
2021-01-13 DRC fixes.
    [Fast_Servo.PrjPCB]
2021-01-24 Fixed length matching of diff pairs for ADC. Length matched to < 10 mm length difference.
2021-03-16 Adding template project for TE7020. PCB file changed, but no modifications were made from previous commit, pushing just for safety.
2021-06-17 Outjob update
    [FastServo.PcbLib, FastServo.SchLib, Fast_Servo.PrjPCB, OK6010_DB.SCHLIB]
2021-11-07 v1.0rc3 added thermal protection
    [ADC_AUX.SchDoc, DAC_AUX.SchDoc, DIGITAL_INPUTS.SchDoc, DIGITAL_IOs.SchDoc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]
2021-11-11 fixed #49 #50
    [Fast_Servo.PrjPCB, PWR_SMPS.SchDoc]
